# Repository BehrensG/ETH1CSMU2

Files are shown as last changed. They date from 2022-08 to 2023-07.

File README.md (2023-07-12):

# ETH1CSMU2
> Yet another poor man's SMU based on LT1970 Power Op Amp.

## What is a SMU ?

A Source Measurement Unit (SMU) is a versatile electronic instrument used in various applications, particularly in the field of electronics testing and characterization. It combines the functionalities of both a voltage source and a current measurement device.

## What is ETH1CSMU2 ?

ETH1CSMU2 is an ongoing hobby project focused on the development of a cost-effective Source Measurement Unit (SMU). The PCB has been designed in accordance with the Eurocard standard size, measuring 160x100 mm. It should be noted that the PCB is intended for integration with a Backplane, such as the [DIN41612_Backplane](https://github.com/BehrensG/DIN41612_Backplane), and is not intended for standalone operation (but it can be).
The PCB requires 24V DC supply. The device can sink and source voltage and current. Can generate a AC sine signal. The PCB includes pars of two ADCs for measurements. 2xADS868 designed the DC output mode, 2xAD7980 designed for AC output mode.

## Parameters

### DC
- Voltage output 11V (bipolar)
- Minimal set voltage step 1mV
- Current ranges 200uA, 2mA, 20mA and 200mA (bipolar)

### AC

- Sine wave generator
- Amplitude 6 V (bipolar)
- Offset 11 V (bipolar)
- Frequency 200 kHz

## Resources
- SCPI parser - https://github.com/j123b567/scpi-parser
- KiCAD - https://www.kicad.org
- STM32CubeIDE - https://www.st.com/en/development-tools/stm32cubeide.html
- POOR MAN'S SMU - https://poormanssmu.wordpress.com
- FreeRTOS - https://www.freertos.org/

## Images
<p align="center"> ETH1CSMU2 </p>

<p align="center">
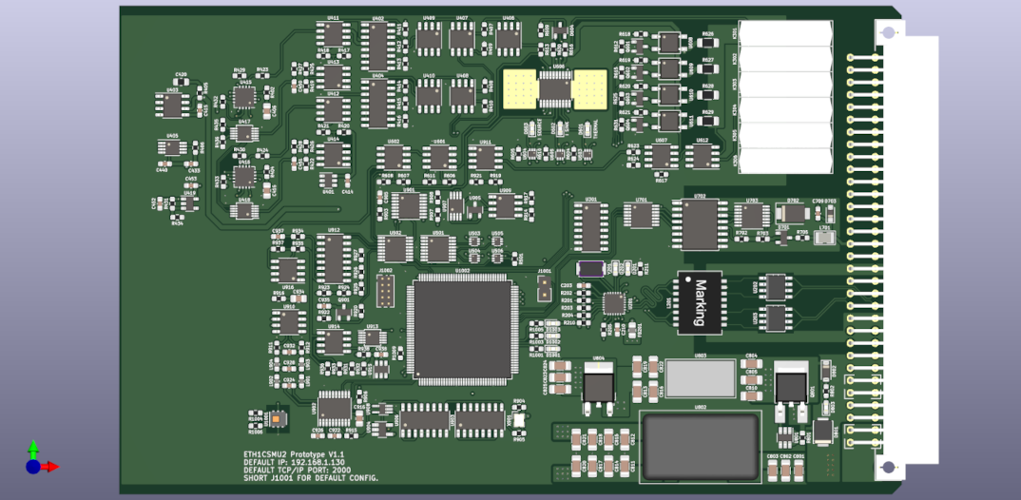
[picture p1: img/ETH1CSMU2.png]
  
 </p>

<p align="center"> Examples of the output voltages </p>

<p align="center">
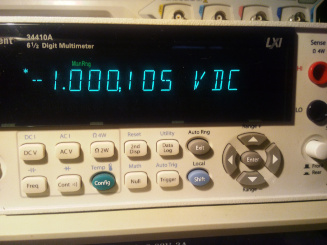
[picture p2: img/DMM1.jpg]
  
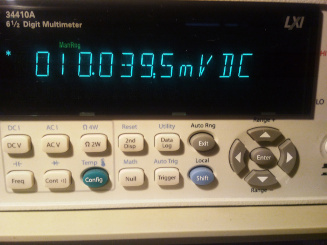
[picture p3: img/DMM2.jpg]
   
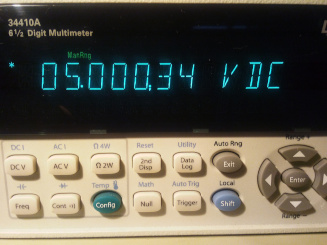
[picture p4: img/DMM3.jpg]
   
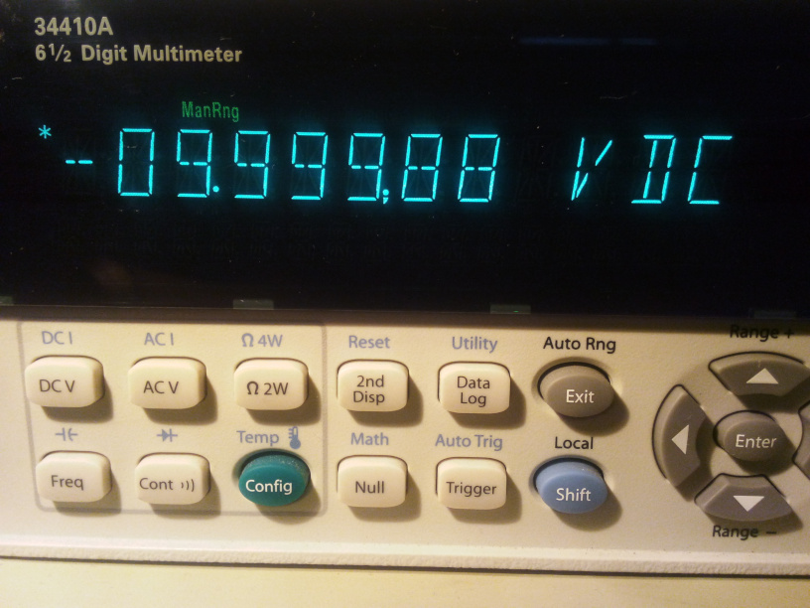
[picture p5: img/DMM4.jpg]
   
 </p>

## Status

Project is ongoing. 

#### TBD:
1. Missing code for ADCs calibration.
2. Missing code for the trigger circuit. 
3. Need to improve the AC code.
4. More images in this README file.
5. Missing SCPI commands documentation.

**<span style="color:red">NOTE</span>**: When using KiCAD project it will be required to change the schematic and PCB libraries paths.

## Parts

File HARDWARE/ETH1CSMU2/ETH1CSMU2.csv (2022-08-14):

Id | Designator | Package | Quantity | Designation | Supplier and ref
1 | C410,C421,C454,C705,C933,C301,C403,C414,C1021,C702,C455,C707,C1010,C415 | C_0603_1608Metric_Pad1.08x0.95mm_HandSolder | 14 | 1u
2 | C449,C617,C441,C903,C912,C603,C428,C419,C405,C919,C928,C601,C426,C929,C402,C507,C445,C418,C435,C606,C446,C612,C907,C429,C1022,C436,C607,C604,C610,C407,C440,C437,C1011,C508,C1018,C425,C605,C438,C704,C434,C611,C908,C1001,C923,C703,C922,C501,C442,C618,C401,C1017,C614,C911,C915,C904,C424,C1014,C901,C708,C906,C444,C417,C510,C430,C502,C608,C615,C616,C413,C918,C1016,C1012,C509,C409,C506,C921,C905,C443,C422,C1015,C926,C1020,C503,C609,C427,C1007,C431,C909,C1004,C448,C504,C1013,C408,C411,C447,C902,C423,C1009,C432,C439,C925,C412,C701,C602,C505,C613,C1019,C1002,C706,C404 | C_0603_1608Metric_Pad1.08x0.95mm_HandSolder | 110 | 100n
3 | R902,R622,R629,R424,R409,R615,R434,R423,R410,R918,R623,R613 | R_0603_1608Metric_Pad0.98x0.95mm_HandSolder | 12 | 0
4 | U604,U503,U505,U506,U603,U605,U504 | SOT-563 | 7 | SN74LVC1T45DRLR
5 | L701 | CW252016 | 1 | CW252016-R33G
6 | R924,R903,R911 | R_0603_1608Metric_Pad0.98x0.95mm_HandSolder | 3 | 68
7 | Y1001 | NX3225GD | 1 | NX5032GA-16.000M
8 | R704,R609,R914,R930,R501,R604,R605,R603,R618,R602,R619,R601,R620,R912,R617 | R_0603_1608Metric_Pad0.98x0.95mm_HandSolder | 15 | 1k
9 | R608,R610,R612 | R_0603_1608Metric_Pad0.98x0.95mm_HandSolder | 3 | 10k2/.1%
10 | C804,C801 | C_1206_3216Metric_Pad1.33x1.80mm_HandSolder | 2 | 10u/50V
11 | K304,K305,K302,K301,K306,K303 | HE360_x-5050462-8 | 6 | HE3621A0510
12 | R212 | R_0603_1608Metric_Pad0.98x0.95mm_HandSolder | 1 | 12k1
13 | U908 | MSOP-8_3x3mm_P0.65mm | 1 | MAX5217GUA+
14 | R206,R611,R211,R1010,R936,R432,R431,R403,R624,R207,R614,R430,R1009,R1002,R917,R208,R935,R701,R630,R429,R209,R401,R203 | R_0603_1608Metric_Pad0.98x0.95mm_HandSolder | 23 | 10k
15 | U1003 | MSOP-8_3x3mm_P0.65mm | 1 | 24LC08B-E/MS
16 | R202,R204,R201,R205,R925 | R_0603_1608Metric_Pad0.98x0.95mm_HandSolder | 5 | 33
17 | C824,C820,C821,C823,C822,C826,C819 | C_1206_3216Metric_Pad1.33x1.80mm_HandSolder | 7 | 1u
18 | U801 | SOT-23-6_Handsoldering | 1 | MAX5902
19 | R706 | R_0603_1608Metric_Pad0.98x0.95mm_HandSolder | 1 | 51R1
20 | D1001 | LED_0603_1608Metric_Pad1.05x0.95mm_HandSolder | 1 | BLUE
21 | R921,R923 | R_0603_1608Metric_Pad0.98x0.95mm_HandSolder | 2 | 220
22 | L904,L903,L901,L902 | L_0603_1608Metric_Pad1.05x0.95mm_HandSolder | 4 | CBMF1608T100K
23 | R414,R411 | R_0603_1608Metric_Pad0.98x0.95mm_HandSolder | 2 | 180k/0.05%
24 | U910,U612,U916 | SOIC-8_3.9x4.9mm_P1.27mm | 3 | LM7171BIM
25 | C213,C214 | C_1206_3216Metric_Pad1.33x1.80mm_HandSolder | 2 | 1n/1kV
26 | R1007,R1006,R905,R919,R1008,R906,R1004,R901 | R_0603_1608Metric_Pad0.98x0.95mm_HandSolder | 8 | 4k7
27 | R607,R606 | R_0603_1608Metric_Pad0.98x0.95mm_HandSolder | 2 | 3k4/.1%
28 | U803 | TSR2 | 1 | TSR2-2450
29 | U404,U402 | SOIC-16_3.9x9.9mm_P1.27mm | 2 | DG444DY+
30 | J1001 | PinHeader_1x02_P2.54mm_Vertical | 1 | Conn_02x01
31 | C825 | C_1206_3216Metric_Pad1.33x1.80mm_HandSolder | 1 | 10u
32 | R908,R907 | R_0603_1608Metric_Pad0.98x0.95mm_HandSolder | 2 | 200/.1%
33 | C210,C205,C202,C208,C212,C209,C211 | C_0201_0603Metric_Pad0.64x0.40mm_HandSolder | 7 | 100n
34 | C204,C201 | C_0201_0603Metric_Pad0.64x0.40mm_HandSolder | 2 | 8p
35 | Q901 | SOT-23 | 1 | FDV301N
36 | U415,U416 | QFN-16-1EP_4x4mm_P0.65mm_EP2.7x2.7mm | 2 | ADS8681IRUMT
37 | U606 | HTSSOP-20-1EP_4.4x6.5mm_P0.65mm_EP3.4x6.5mm_ThermalVias | 1 | LT1970ACFE
38 | C452,C453 | C_0603_1608Metric_Pad1.08x0.95mm_HandSolder | 2 | 2n7
39 | C207,C206 | C_0201_0603Metric_Pad0.64x0.40mm_HandSolder | 2 | 1u
40 | U610,U611,U609,U608 | AQY212GS | 4 | AQY212G2SX
41 | R703,R926 | R_0603_1608Metric_Pad0.98x0.95mm_HandSolder | 2 | 100
42 | U703 | TSSOP-14_4.4x5mm_P0.65mm | 1 | 74AC125
43 | U413,U911,U410,U409,U414 | SOIC-8_3.9x4.9mm_P1.27mm | 5 | OPA141AID
44 | C811,C814,C812 | C_1206_3216Metric_Pad1.33x1.80mm_HandSolder | 3 | 22u
45 | C932,C931,C924 | C_0603_1608Metric_Pad1.08x0.95mm_HandSolder | 3 | 1p
46 | R929 | R_0603_1608Metric_Pad0.98x0.95mm_HandSolder | 1 | 26k4
47 | D702 | D_SMB | 1 | SMBJ5.0A
48 | J301 | Socket_DIN41612-CaseC1-AC-Male-64Pin-2rows | 1 | C64AC
49 | C805,C817,C802,C810,C813,C803 | C_1206_3216Metric_Pad1.33x1.80mm_HandSolder | 6 | 4u7/50V
50 | U912 | MSOP-10_3x3mm_P0.5mm | 1 | AD5322ARMZ
51 | C203 | C_0201_0603Metric_Pad0.64x0.40mm_HandSolder | 1 | 470p
52 | U913 | SOIC-16_3.9x9.9mm_P1.27mm | 1 | DG409DY+
53 | D602,D1002,D603,D803,D601 | LED_0603_1608Metric_Pad1.05x0.95mm_HandSolder | 5 | RED
54 | D202,D1003 | LED_0603_1608Metric_Pad1.05x0.95mm_HandSolder | 2 | GREEN
55 | C450,C451 | C_0603_1608Metric_Pad1.08x0.95mm_HandSolder | 2 | 330p
56 | R427,R428 | R_0603_1608Metric_Pad0.98x0.95mm_HandSolder | 2 | 20
57 | R407,R801,R931,R408,R920 | R_0603_1608Metric_Pad0.98x0.95mm_HandSolder | 5 | 100k
58 | U403 | SOIC-8_3.9x4.9mm_P1.27mm | 1 | REF5040ID
59 | R406 | R_0603_1608Metric_Pad0.98x0.95mm_HandSolder | 1 | 82k
60 | R214,R213 | R_0603_1608Metric_Pad0.98x0.95mm_HandSolder | 2 | 270
61 | R422,R421,R418,R419 | R_0603_1608Metric_Pad0.98x0.95mm_HandSolder | 4 | 12k/.1%
62 | R904 | R_0603_1608Metric_Pad0.98x0.95mm_HandSolder | 1 | 7k5
63 | R217,R218,R216,R215 | R_0603_1608Metric_Pad0.98x0.95mm_HandSolder | 4 | 49R9
64 | R1001,R1005,R922 | R_0603_1608Metric_Pad0.98x0.95mm_HandSolder | 3 | 680
65 | U906 | SOT-23 | 1 | MAX6102EUR
66 | R932,R909,R934,R933,R910 | R_0603_1608Metric_Pad0.98x0.95mm_HandSolder | 5 | 1k/.1%
67 | U1002 | TQFP-144_20x20mm_P0.5mm | 1 | STM32F746ZG
68 | Q604,Q601,Q602,Q603 | SOT-23 | 4 | MMBT3904
69 | X901 | IQXO-791 | 1 | 830208220601
70 | C1006,C1008 | C_0603_1608Metric_Pad1.08x0.95mm_HandSolder | 2 | 2u2
71 | U502,U501 | TSSOP-16_4.4x5mm_P0.65mm | 2 | 74HCT595PW
72 | U419 | SOT-23-5 | 1 | TPS76925
73 | U405 | MSOP-8_3x3mm_P0.65mm | 1 | ADR435ARM
74 | U804 | TO-252-2 | 1 | NCV1117DT33T5G
75 | FB1001,FB201 | L_0805_2012Metric_Pad1.15x1.40mm_HandSolder | 2 | 742792031
76 | R220,R221 | R_0603_1608Metric_Pad0.98x0.95mm_HandSolder | 2 | 75/1%
77 | U407,U602,U411,U412,U601,U406,U408 | SOIC-8_3.9x4.9mm_P1.27mm | 7 | DG419DY
78 | U702 | SOIC-16W_7.5x10.3mm_P1.27mm | 1 | ADuM5402
79 | R627 | R_1206_3216Metric_Pad1.30x1.75mm_HandSolder | 1 | RQ73C2B100RBT
80 | D701 | SOT-23 | 1 | BAV99
81 | R915,R913 | R_0603_1608Metric_Pad0.98x0.95mm_HandSolder | 2 | 20k/.1%
82 | D201 | LED_0603_1608Metric_Pad1.05x0.95mm_HandSolder | 1 | YELLOW
83 | R402,R404,R405 | R_0603_1608Metric_Pad0.98x0.95mm_HandSolder | 3 | 0R22
84 | C1005,C1003 | C_0603_1608Metric_Pad1.08x0.95mm_HandSolder | 2 | 8p
85 | U701 | TSSOP-14_4.4x5mm_P0.65mm | 1 | TXB0104PW
86 | C927 | C_0805_2012Metric_Pad1.18x1.45mm_HandSolder | 1 | 4u7/OPT
87 | U905,U902 | SOIC-16_3.9x9.9mm_P1.27mm | 2 | MC74AC161DR2G
88 | R802 | R_0603_1608Metric_Pad0.98x0.95mm_HandSolder | 1 | 330
89 | R415,R412 | R_0603_1608Metric_Pad0.98x0.95mm_HandSolder | 2 | 18k/0.05%
90 | F801 | Fuse_SMD2920 | 1 | MF-LSMF185/33X
91 | C621,C620,C622,C619 | C_0603_1608Metric_Pad1.08x0.95mm_HandSolder | 4 | 10p
92 | C433,C913,C916,C930 | C_0603_1608Metric_Pad1.08x0.95mm_HandSolder | 4 | 10n
93 | U914 | SOIC-8_3.9x4.9mm_P1.27mm | 1 | TL071CDR
94 | U915,U401 | TSOT-23-6 | 2 | LT1790BCS6-2.5
95 | C818,C816,C815 | C_1206_3216Metric_Pad1.33x1.80mm_HandSolder | 3 | 4u7
96 | R928 | R_0603_1608Metric_Pad0.98x0.95mm_HandSolder | 1 | 20k8
97 | D802 | D_SOD-123 | 1 | MMSZ5249B
98 | R417,R425,R420,R426 | R_0603_1608Metric_Pad0.98x0.95mm_HandSolder | 4 | 2k49/.1%
99 | U901 | TSSOP-16_4.4x5mm_P0.65mm | 1 | DAC8565ICPW
100 | C917 | C_0603_1608Metric_Pad1.08x0.95mm_HandSolder | 1 | 68p
101 | U417,U418 | MSOP-10_3x3mm_P0.5mm | 2 | AD7980ARM
102 | U907 | SOT-353_SC-70-5_Handsoldering | 1 | SN74AUP1G79DCKR
103 | C809,C808,C807,C806 | C_1206_3216Metric_Pad1.33x1.80mm_HandSolder | 4 | 1000p/2kV
104 | R702 | R_0603_1608Metric_Pad0.98x0.95mm_HandSolder | 1 | 14k7
105 | C920,C914 | C_0603_1608Metric_Pad1.08x0.95mm_HandSolder | 2 | 100p
106 | D703 | D_SOD-323_HandSoldering | 1 | SD36C-01FTG
107 | C416,C406 | R_0805_2012Metric_Pad1.20x1.40mm_HandSolder | 2 | 22u
108 | R416,R413 | R_0603_1608Metric_Pad0.98x0.95mm_HandSolder | 2 | 2k/0.05%
109 | R705 | R_0603_1608Metric_Pad0.98x0.95mm_HandSolder | 1 | 47
110 | Y201 | NX5032GA | 1 | NX5032GA-25.000000MHZ-LN-CD-1
111 | U203,U202 | SO8E | 2 | LC03-3.3
112 | R927 | R_0603_1608Metric_Pad0.98x0.95mm_HandSolder | 1 | 200
113 | C827 | C_1206_3216Metric_Pad1.33x1.80mm_HandSolder | 1 | 100n
114 | D801 | DO_214AA_REV | 1 | SM6T30AY
115 | R433,R621 | R_0603_1608Metric_Pad0.98x0.95mm_HandSolder | 2 | OPT
116 | R210 | R_0603_1608Metric_Pad0.98x0.95mm_HandSolder | 1 | 1k5
117 | U904 | SOT-23-5_HandSoldering | 1 | SN74AHC1G14DBVT
118 | R916 | R_0603_1608Metric_Pad0.98x0.95mm_HandSolder | 1 | 1Meg
119 | R625 | R_1206_3216Metric_Pad1.30x1.75mm_HandSolder | 1 | RT1206BRD071RL
120 | U607 | SOIC-8_3.9x4.9mm_P1.27mm | 1 | INA823DT
121 | U909 | SOIC-8_3.9x4.9mm_P1.27mm | 1 | OPA2141AID
122 | C420 | R_0805_2012Metric_Pad1.20x1.40mm_HandSolder | 1 | 10u
123 | U1001 | Texas_PWSON-N6 | 1 | HDC1080
124 | U903 | TSSOP-20_4.4x6.5mm_P0.65mm | 1 | AD9834BRUZ
125 | J1002 | PinHeader_2x05_P1.27mm_Vertical | 1 | 20021111-00010T4LF
126 | R219 | R_1206_3216Metric_Pad1.30x1.75mm_HandSolder | 1 | 1M/1kV
127 | U201 | QFN-24-1EP_4x4mm_P0.5mm_EP2.6x2.6mm_ThermalVias | 1 | LAN8742A
128 | U802 | TEL12-DUAL | 1 | TEL 12-2423
129 | L201 | 749010012A | 1 | 749010012A
130 | R1003 | R_0603_1608Metric_Pad0.98x0.95mm_HandSolder | 1 | 560
131 | R628 | R_1206_3216Metric_Pad1.30x1.75mm_HandSolder | 1 | PHPA1206E1001BST
132 | C709 | C_0603_1608Metric_Pad1.08x0.95mm_HandSolder | 1 | 47p
133 | Q801 | TO-252-2_Rectifier | 1 | IRFR5410
134 | R626 | R_1206_3216Metric_Pad1.30x1.75mm_HandSolder | 1 | RP73D2B10RBTG
135 | U301 | SOIC-16_3.9x9.9mm_P1.27mm | 1 | ULN2003AIDE4
136 | C910 | C_0805_2012Metric_Pad1.18x1.45mm_HandSolder | 1 | 4u7
137 | R616 | R_0603_1608Metric_Pad0.98x0.95mm_HandSolder | 1 | 11k/.1%

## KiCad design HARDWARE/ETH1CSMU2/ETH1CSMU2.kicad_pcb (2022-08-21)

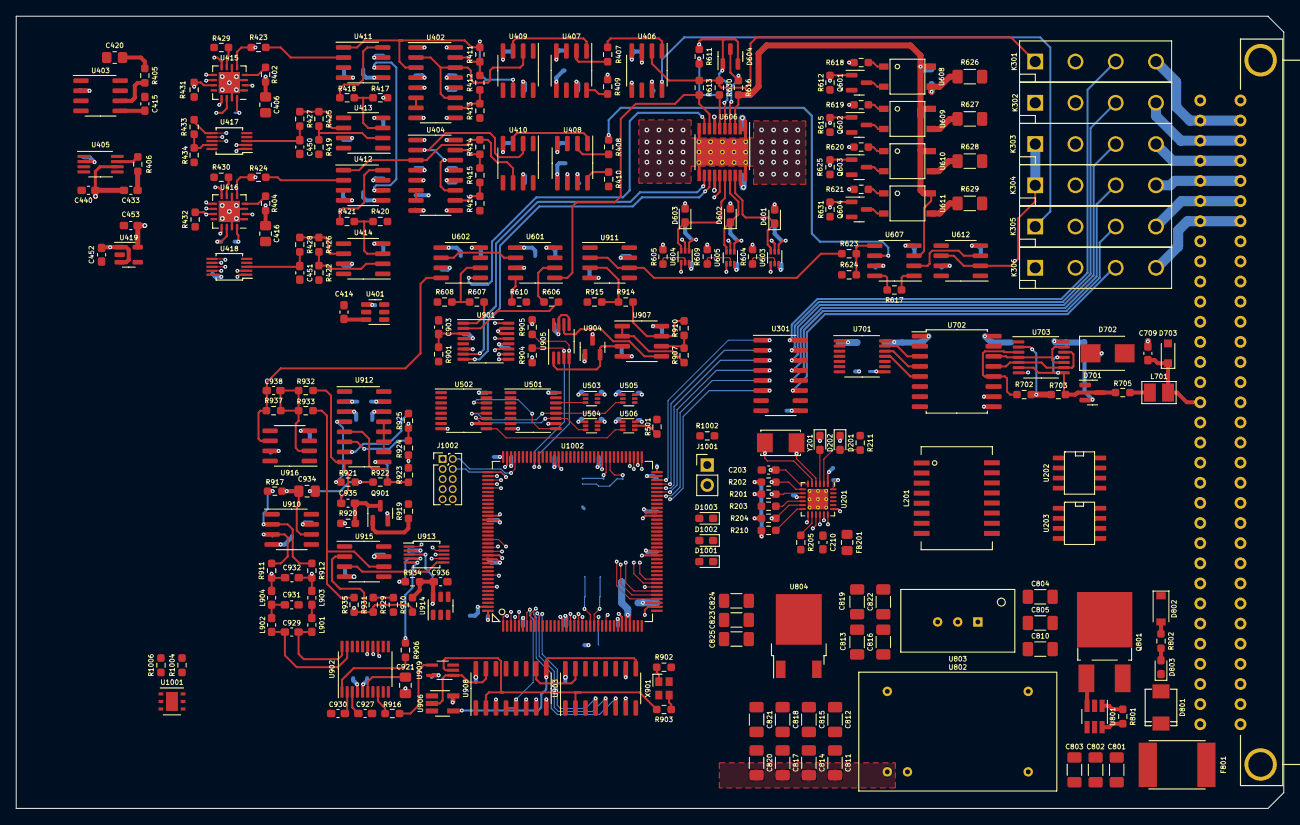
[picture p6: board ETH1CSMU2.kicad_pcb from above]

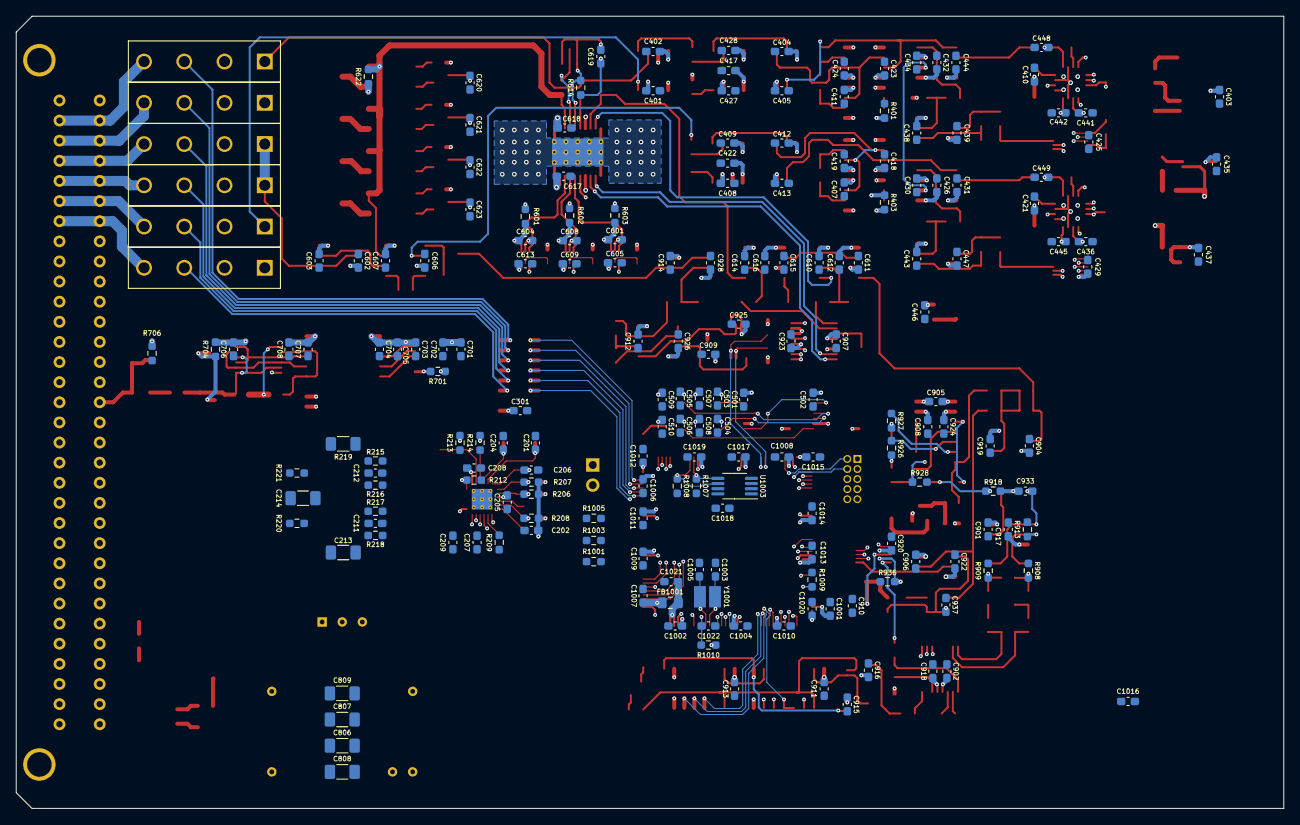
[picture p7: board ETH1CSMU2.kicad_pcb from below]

Board: 4 copper layers, 160.0 x 100.0 mm, 446 parts (191 on the bottom side), 310 nets.

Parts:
C201, C204, C1003, C1005: 8p; C_0603_1608Metric_Pad1.08x0.95mm_HandSolder
C202, C205, C208, C209, C210, C211, C212, C401, C402, C404, C405, C407, C408, C409, C411, C412, C413, C417, C418, C419, C422, C423, C424, C425, C426, C427, C428, C429, C430, C431, C432, C434, C435, C436, C437, C438, C439, C440, C441, C442, C443, C444, C445, C446, C447, C501, C502, C503, C504, C505, C506, C507, C508, C509, C510, C601, C602, C603, C604, C605, C606, C607, C608, C609, C610, C611, C612, C613, C614, C615, C616, C617, C618, C701, C703, C704, C706, C708, C901, C902, C903, C904, C905, C906, C907, C908, C909, C910, C911, C912, C913, C914, C915, C916, C917, C918, C919, C920, C922, C923, C924, C925, C926, C928, C1001, C1002, C1004, C1007, C1009, C1011, C1012, C1013, C1014, C1015, C1016, C1017, C1018, C1019, C1020, C1022: 100n; C_0603_1608Metric_Pad1.08x0.95mm_HandSolder
C203: 470p; C_0603_1608Metric_Pad1.08x0.95mm_HandSolder
C206, C207, C301, C403, C410, C414, C415, C421, C452, C453, C702, C705, C707, C936, C1010, C1021: 1u; C_0603_1608Metric_Pad1.08x0.95mm_HandSolder
C213, C214: 1n/1kV; C_1206_3216Metric_Pad1.33x1.80mm_HandSolder
C406, C416: 22u; R_0805_2012Metric_Pad1.20x1.40mm_HandSolder
C420: 10u; R_0805_2012Metric_Pad1.20x1.40mm_HandSolder
C433, C927, C930, C935: 10n; C_0603_1608Metric_Pad1.08x0.95mm_HandSolder
C448, C449: 330p; C_0603_1608Metric_Pad1.08x0.95mm_HandSolder
C450, C451: 2n7; C_0603_1608Metric_Pad1.08x0.95mm_HandSolder
C619: 1n; C_0603_1608Metric_Pad1.08x0.95mm_HandSolder
C620, C621, C622, C623: 10p; C_0603_1608Metric_Pad1.08x0.95mm_HandSolder
C709: 47p; C_0603_1608Metric_Pad1.08x0.95mm_HandSolder
C801, C804: 10u/50V; C_1206_3216Metric_Pad1.33x1.80mm_HandSolder
C802, C803, C805, C810: 4u7/50V; C_1206_3216Metric_Pad1.33x1.80mm_HandSolder
C806, C807, C808, C809: 1000p/2kV; C_1206_3216Metric_Pad1.33x1.80mm_HandSolder
C811, C812, C813: 22u; C_1206_3216Metric_Pad1.33x1.80mm_HandSolder
C814, C815, C816: 4u7; C_1206_3216Metric_Pad1.33x1.80mm_HandSolder
C817, C818, C819, C820, C821, C822, C824: 1u; C_1206_3216Metric_Pad1.33x1.80mm_HandSolder
C823: 10u; C_1206_3216Metric_Pad1.33x1.80mm_HandSolder
C825: 100n; C_1206_3216Metric_Pad1.33x1.80mm_HandSolder
C921: 4u7; C_0805_2012Metric_Pad1.18x1.45mm_HandSolder
C929, C932: 100p; C_0603_1608Metric_Pad1.08x0.95mm_HandSolder
C931: 68p; C_0603_1608Metric_Pad1.08x0.95mm_HandSolder
C933, C937, C938: 1p; C_0603_1608Metric_Pad1.08x0.95mm_HandSolder
C934: 4u7/OPT; C_0805_2012Metric_Pad1.18x1.45mm_HandSolder
C1006, C1008: 2u2; C_0603_1608Metric_Pad1.08x0.95mm_HandSolder
D201: YELLOW; LED_0603_1608Metric_Pad1.05x0.95mm_HandSolder
D202, D1003: GREEN; LED_0603_1608Metric_Pad1.05x0.95mm_HandSolder
D601, D602, D603, D803, D1002: RED; LED_0603_1608Metric_Pad1.05x0.95mm_HandSolder
D604, D701: BAV99; SOT-23
D702: SMBJ5.0A; D_SMB
D703: SD36C-01FTG; D_SOD-323_HandSoldering
D801: SM6T30AY; DO_214AA_REV
D802: MMSZ5249B; D_SOD-123
D1001: BLUE; LED_0603_1608Metric_Pad1.05x0.95mm_HandSolder
F801: MF-LSMF185/33X; Fuse_SMD2920
FB201, FB1001: 742792031; L_0805_2012Metric_Pad1.15x1.40mm_HandSolder
J301: C64AC; Socket_DIN41612-CaseC1-AC-Male-64Pin-2rows
J1001: Conn_02x01; PinHeader_1x02_P2.54mm_Vertical
J1002: 20021111-00010T4LF; PinHeader_2x05_P1.27mm_Vertical
K301, K302, K303, K304, K305, K306: HE3621A0510; HE360_x-5050462-8
L201: 749010012A
L701: CW252016-R33G; CW252016
L901, L902, L903, L904: CBMF1608T100K; L_0603_1608Metric_Pad1.05x0.95mm_HandSolder
Q601, Q602, Q603, Q604: MMBT3904; SOT-23
Q801: IRFR5410; TO-252-2_Rectifier
Q901: FDV301N; SOT-23
R201, R202, R204, R205, R925: 33; R_0603_1608Metric_Pad0.98x0.95mm_HandSolder
R203, R206, R207, R208, R209, R211, R401, R403, R429, R430, R431, R432, R612, R615, R625, R631, R701, R915, R934, R936, R1002, R1009, R1010: 10k; R_0603_1608Metric_Pad0.98x0.95mm_HandSolder
R210: 1k5; R_0603_1608Metric_Pad0.98x0.95mm_HandSolder
R212: 12k1; R_0603_1608Metric_Pad0.98x0.95mm_HandSolder
R213, R214: 270; R_0603_1608Metric_Pad0.98x0.95mm_HandSolder
R215, R216, R217, R218: 49R9; R_0603_1608Metric_Pad0.98x0.95mm_HandSolder
R219: 1M/1kV; R_1206_3216Metric_Pad1.30x1.75mm_HandSolder
R220, R221: 75/1%; R_0603_1608Metric_Pad0.98x0.95mm_HandSolder
R402, R404, R405: 0R22; R_0603_1608Metric_Pad0.98x0.95mm_HandSolder
R406: 82k; R_0603_1608Metric_Pad0.98x0.95mm_HandSolder
R407, R408, R801, R920, R935: 100k; R_0603_1608Metric_Pad0.98x0.95mm_HandSolder
R409, R410, R423, R424, R434, R614, R616, R623, R624, R630, R901, R918: 0; R_0603_1608Metric_Pad0.98x0.95mm_HandSolder
R411, R414: 180k/0.05%; R_0603_1608Metric_Pad0.98x0.95mm_HandSolder
R412, R415: 18k/0.05%; R_0603_1608Metric_Pad0.98x0.95mm_HandSolder
R413, R416: 2k/0.05%; R_0603_1608Metric_Pad0.98x0.95mm_HandSolder
R417, R420, R425, R426: 2k49/.1%; R_0603_1608Metric_Pad0.98x0.95mm_HandSolder
R418, R419, R421, R422: 12k/.1%; R_0603_1608Metric_Pad0.98x0.95mm_HandSolder
R427, R428: 20; R_0603_1608Metric_Pad0.98x0.95mm_HandSolder
R433, R622: OPT; R_0603_1608Metric_Pad0.98x0.95mm_HandSolder
R501, R601, R602, R603, R604, R605, R609, R618, R619, R620, R621, R704, R907, R910, R928: 1k; R_0603_1608Metric_Pad0.98x0.95mm_HandSolder
R606, R607: 3k4/.1%; R_0603_1608Metric_Pad0.98x0.95mm_HandSolder
R608, R610, R613: 10k2/.1%; R_0603_1608Metric_Pad0.98x0.95mm_HandSolder
R611, R703, R926: 100; R_0603_1608Metric_Pad0.98x0.95mm_HandSolder
R617: 11k/.1%; R_0603_1608Metric_Pad0.98x0.95mm_HandSolder
R626: RT1206BRD071RL; R_1206_3216Metric_Pad1.30x1.75mm_HandSolder
R627: RP73D2B10RBTG; R_1206_3216Metric_Pad1.30x1.75mm_HandSolder
R628: RQ73C2B100RBT; R_1206_3216Metric_Pad1.30x1.75mm_HandSolder
R629: PHPA1206E1001BST; R_1206_3216Metric_Pad1.30x1.75mm_HandSolder
R702: 14k7; R_0603_1608Metric_Pad0.98x0.95mm_HandSolder
R705: 47; R_0603_1608Metric_Pad0.98x0.95mm_HandSolder
R706: 51R1; R_0603_1608Metric_Pad0.98x0.95mm_HandSolder
R802: 330; R_0603_1608Metric_Pad0.98x0.95mm_HandSolder
R902, R904, R905, R919, R1004, R1006, R1007, R1008: 4k7; R_0603_1608Metric_Pad0.98x0.95mm_HandSolder
R903, R916, R924: 68; R_0603_1608Metric_Pad0.98x0.95mm_HandSolder
R906: 7k5; R_0603_1608Metric_Pad0.98x0.95mm_HandSolder
R908, R909: 200/.1%; R_0603_1608Metric_Pad0.98x0.95mm_HandSolder
R911, R912, R932, R933, R937: 1k/.1%; R_0603_1608Metric_Pad0.98x0.95mm_HandSolder
R913, R917: 20k/.1%; R_0603_1608Metric_Pad0.98x0.95mm_HandSolder
R914: 1Meg; R_0603_1608Metric_Pad0.98x0.95mm_HandSolder
R921, R923: 220; R_0603_1608Metric_Pad0.98x0.95mm_HandSolder
R922, R1001, R1005: 680; R_0603_1608Metric_Pad0.98x0.95mm_HandSolder
R927: 200; R_0603_1608Metric_Pad0.98x0.95mm_HandSolder
R929: 26k1; R_0603_1608Metric_Pad0.98x0.95mm_HandSolder
R930: 20k8; R_0603_1608Metric_Pad0.98x0.95mm_HandSolder
R931: 300; R_0603_1608Metric_Pad0.98x0.95mm_HandSolder
R1003: 560; R_0603_1608Metric_Pad0.98x0.95mm_HandSolder
U201: LAN8742A; QFN-24-1EP_4x4mm_P0.5mm_EP2.6x2.6mm_ThermalVias
U202, U203: LC03-3.3; SO8E
U301: ULN2003AIDE4; SOIC-16_3.9x9.9mm_P1.27mm
U401, U914: LT1790BCS6-2.5; TSOT-23-6
U402, U404: DG444DY+; SOIC-16_3.9x9.9mm_P1.27mm
U403: REF5040ID; SOIC-8_3.9x4.9mm_P1.27mm
U405: ADR435ARM; MSOP-8_3x3mm_P0.65mm
U406, U407, U408, U411, U412, U601, U602: DG419DY; SOIC-8_3.9x4.9mm_P1.27mm
U409, U410, U413, U414, U911: OPA141AID; SOIC-8_3.9x4.9mm_P1.27mm
U415, U416: ADS8681IRUMT; QFN-16-1EP_4x4mm_P0.65mm_EP2.7x2.7mm
U417, U418: AD7980ARM; MSOP-10_3x3mm_P0.5mm
U419: TPS76925; SOT-23-5
U501, U502: 74HCT595PW; TSSOP-16_4.4x5mm_P0.65mm
U503, U504, U505, U506, U603, U604, U605: SN74LVC1T45DRLR; SOT-563
U606: LT1970ACFE; HTSSOP-20-1EP_4.4x6.5mm_P0.65mm_EP3.4x6.5mm_ThermalVias
U607: INA823DT; SOIC-8_3.9x4.9mm_P1.27mm
U608, U609, U610, U611: AQY212G2SX; AQY212GS
U612, U910, U916: LM7171BIM; SOIC-8_3.9x4.9mm_P1.27mm
U701: TXB0104PW; TSSOP-14_4.4x5mm_P0.65mm
U702: ADuM5402; SOIC-16W_7.5x10.3mm_P1.27mm
U703: 74AC125; TSSOP-14_4.4x5mm_P0.65mm
U801: MAX5902ACEUT; SOT-23-6_Handsoldering
U802: TEL 12-2423; TEL12-DUAL
U803: TSR2-2450; TSR2
U804: NCV1117DT33T5G; TO-252-2
U901: DAC8565ICPW; TSSOP-16_4.4x5mm_P0.65mm
U902: AD9834BRUZ; TSSOP-20_4.4x6.5mm_P0.65mm
U903, U908: MC74AC161DR2G; SOIC-16_3.9x9.9mm_P1.27mm
U904: MAX6102EUR; SOT-23
U905: MAX5217GUA+; MSOP-8_3x3mm_P0.65mm
U906: SN74AHC1G14DBVT; SOT-23-5_HandSoldering
U907: OPA2141AID; SOIC-8_3.9x4.9mm_P1.27mm
U909: SN74AUP1G79DCKR; SOT-353_SC-70-5_Handsoldering
U912: DG409DY+; SOIC-16_3.9x9.9mm_P1.27mm
U913: AD5322ARMZ; MSOP-10_3x3mm_P0.5mm
U915: TL071CDR; SOIC-8_3.9x4.9mm_P1.27mm
U1001: HDC1080; Texas_PWSON-N6
U1002: STM32F746ZG; TQFP-144_20x20mm_P0.5mm
U1003: 24LC08B-E/MS; MSOP-8_3x3mm_P0.65mm
X901: 830208220601; IQXO-791
Y201: NX5032GA-25.000000MHZ-LN-CD-1; NX5032GA
Y1001: NX5032GA-16.000M; NX3225GD

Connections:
+1V25: R934.2, R936.2, U913.4 (VREFA)
+2V5PWR: C453.1, U417.2 (VDD), U418.2 (VDD), U419.5 (OUT)
+3.3V: C202.1, C205.1, C425.1, C429.1, C436.1, C441.1, C507.1, C508.1, C509.1, C510.1, C605.1, C609.1, C613.1, C701.1, C702.1, C823.1, C824.1, C825.1, C911.1, C913.1, C915.1, C916.1, C918.1, C920.1, C923.1, C925.1, C1001.1, C1002.1, C1004.1, C1007.1, C1009.1, C1010.1, C1011.1, C1012.1, C1013.1, C1014.1, C1015.1, C1016.1, C1017.1, C1018.1, C1019.1, C1020.1, D1001.2 (A), D1002.2 (A), D1003.2 (A), FB201.2, FB1001.2, J1002.1, R206.1, R207.1, R208.1, R209.1, R210.1, R429.1, R430.1, R431.1, R432.1, R701.1, R902.1, R904.1, R905.1, R1002.2, R1004.1, R1006.1, R1007.1, R1008.1, R1010.1, U201.9 (VDDIO), U415.14 (DVDD), U416.14 (DVDD), U417.10 (VIO), U418.10 (VIO), U503.6 (VCCB), U504.6 (VCCB), U505.6 (VCCB), U506.6 (VCCB), U603.6 (VCCB), U604.6 (VCCB), U605.6 (VCCB), U701.1 (VCCA), U804.2 (VO), U901.12 (IOVDD), U902.5 (DVDD), U903.1 (~MR), U903.7 (CEP), U903.10 (CET), U903.16 (VCC), U905.5 (~AUX), U905.7 (VDD), U906.5 (VCC), U908.1 (~MR), U908.3 (P0), U908.6 (P3), U908.7 (CEP), U908.16 (VCC), U909.5 (VCC), U913.2 (VDD), U1001.5 (VCC), U1002.6 (VBAT), U1002.17 (VDD), U1002.30 (VDD), U1002.39 (VDD), U1002.52 (VDD), U1002.62 (VDD), U1002.72 (VDD), U1002.84 (VDD), U1002.95 (VDDUSB), U1002.108 (VDD), U1002.121 (VDD), U1002.131 (VDD), U1002.143 (PDR_ON), U1002.144 (VDD), U1003.8 (VCC), X901.4 (VDD)
+4V: R405.1, U403.6 (Vout), U415.2 (REFIO), U416.2 (REFIO)
+5V: C301.1, C403.1, C407.1, C411.1, C417.1, C422.1, C426.1, C432.1, C437.1, C442.1, C445.1, C452.1, C501.1, C502.1, C503.1, C504.1, C505.1, C506.1, C601.1, C604.1, C608.1, C612.1, C616.1, C703.1, C704.1, C705.1, C813.1, C816.1, C819.1, C822.1, C902.1, C905.1, C907.1, C909.1, C927.1, K301.2, K302.2, K303.2, K304.2, K305.2, K306.2, R401.2, R403.2, R501.2, R601.1, R602.1, R603.1, R604.2, R605.2, R609.2, R618.1, R619.1, R620.1, R621.1, R920.1, U301.9 (COM), U402.12 (VL), U403.2 (Vin), U404.12 (VL), U406.5 (VL), U407.5 (VL), U408.5 (VL), U411.5 (VL), U412.5 (VL), U415.16 (AVDD), U416.16 (AVDD), U419.1 (IN), U419.3 (~EN), U501.10 (~SRCLR), U501.16 (VCC), U502.10 (~SRCLR), U502.16 (VCC), U503.1 (VCCA), U504.1 (VCCA), U505.1 (VCCA), U506.1 (VCCA), U601.5 (VL), U602.5 (VL), U603.1 (VCCA), U604.1 (VCCA), U605.1 (VCCA), U701.14 (VCCB), U702.1 (VDD1), U803.3 (VO), U804.3 (VI), U901.4 (AVDD), U902.4 (AVDD), U904.1 (IN), U912.2 (EN)
+5VREF: C433.1, C440.1, U405.6 (VOUT), U417.1 (REF), U418.1 (REF)
+5V_TRIG: C706.1, C707.1, C708.1, R704.1, U702.10 (VSEL), U702.16 (VISO), U703.14 (VCC)
+15V: C402.1, C405.1, C409.1, C413.1, C419.1, C424.1, C428.1, C431.1, C435.1, C439.1, C444.1, C446.1, C447.1, C602.1, C606.1, C610.1, C614.1, C617.1, C807.2, C809.2, C811.1, C814.1, C817.1, C820.1, C901.1, C904.1, C906.1, C908.1, C910.1, C912.1, C914.1, U401.4 (Vin), U402.13 (V+), U404.13 (V+), U405.2 (VIN), U406.4 (V+), U407.4 (V+), U408.4 (V+), U409.7 (V+), U410.7 (V+), U411.4 (V+), U412.4 (V+), U413.7 (V+), U414.7 (V+), U601.4 (V+), U602.4 (V+), U606.7 (VCC), U606.19 (V+), U607.7 (V+), U612.7 (V+), U802.9 (+VOUT), U907.8 (V+), U910.7 (V+), U911.7 (V+), U912.14 (V+), U914.4 (Vin), U915.7 (V+), U916.7 (V+)
+24V: F801.2, J301.A31 (31A), J301.A32 (32A), J301.C31 (31C), J301.C32 (32C)
-15V: C401.1, C404.1, C408.1, C412.1, C418.1, C423.1, C427.1, C430.1, C434.1, C438.1, C443.1, C603.1, C607.1, C611.1, C615.1, C618.1, C806.2, C808.2, C812.2, C815.2, C818.2, C821.2, C917.1, C919.1, C922.1, C924.1, C926.1, C928.1, U402.4 (V-), U404.4 (V-), U406.7 (V-), U407.7 (V-), U408.7 (V-), U409.4 (V-), U410.4 (V-), U411.7 (V-), U412.7 (V-), U413.4 (V-), U414.4 (V-), U601.7 (V-), U602.7 (V-), U606.1 (VEE), U606.2 (V-), U606.10 (VEE), U606.11 (VEE), U606.20 (VEE), U606.21 (VEE), U607.4 (V-), U612.4 (V-), U802.10 (-VOUT), U907.4 (V-), U910.4 (V-), U911.4 (V-), U912.3 (V-), U915.4 (V-), U916.4 (V-)
/Connect/A: J301.A2 (2A), J301.C2 (2C), K301.4
/Connect/B: J301.A3 (3A), J301.C3 (3C), K302.4
/Connect/C: J301.A4 (4A), J301.C4 (4C), K303.4
/Connect/CXN_REL1: U301.1 (I1), U1002.70 (PB11,TIM2_CH4,I2C2_SDA,DFSDM1_CKIN7,USA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)
/Connect/CXN_REL2: U301.2 (I2), U1002.69 (PB10,TIM2_CH3,I2C2_SCL,SPI2_SCK,I2S2_CK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)
/Connect/CXN_REL3: U301.3 (I3), U1002.68 (PE15,TIM1_BKIN,FMC_D12,LCD_R7,EVENTOUT)
/Connect/CXN_REL4: U301.4 (I4), U1002.67 (PE14,TIM1_CH4,SPI4_MOSI,SAI2_MCLK_B,FMC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)
/Connect/CXN_REL5: U301.5 (I5), U1002.66 (PE13,TIM1_CH3,SPI4_MISO,DFSDM1_CKIN5,SA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)
/Connect/CXN_REL6: U301.6 (I6), U1002.65 (PE12,TIM1_CH3N,SPI4_SCK,DFSDM1_DATIN5,S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)
/Connect/D: J301.A5 (5A), J301.C5 (5C), K304.4
/Connect/E: J301.A6 (6A), J301.C6 (6C), K305.4
/Connect/EXT_TRIG: C709.1, D703.1 (A1), J301.A16 (16A), L701.1
/Connect/F: J301.A7 (7A), J301.C7 (7C), K306.4
/Connect/GUARD: K303.1, K304.1, U612.2 (-), U612.6
/Connect/RX+: J301.A20 (20A), U203.8
/Connect/RX-: J301.A21 (21A), U203.5
/Connect/TX+: J301.C20 (20C), U202.8
/Connect/TX-: J301.C21 (21C), U202.5
/Connect/VOLT_MEAS_SENS: K305.1, U406.8
/Connect/VOUT_OUT: K301.1, R613.2, R626.2, R627.2, R628.2, R629.2, R630.1, U406.2, U607.2 (-), U612.3 (+)
/Control/ATT_A0: U502.3 (QD), U912.1 (A0)
/Control/ATT_A1: U502.4 (QE), U912.16 (A1)
/Control/C_AZ: U408.6, U501.7 (QH)
/Control/C_G1: U404.1, U501.4 (QE)
/Control/C_G10: U404.16, U501.5 (QF)
/Control/C_G100: U404.9, U501.6 (QG)
/Control/DDS_LPF: R919.2, U502.5 (QF)
/Control/MCU_ENA: U502.15 (QA), U606.15 (ENA)
/Control/SING_SEL: U502.2 (QC), U601.6, U602.6
/Control/SR_CLK: U504.4 (B), U1002.117 (PD3,DFSDM1_CKOUT,SPI2_SCK,I2S2_CK,DFSDM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)
/Control/SR_DAT: U503.4 (B), U1002.118 (PD4,DFSDM1_CKIN0,USART2_RTS,FMC_NOE,EVE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)
/Control/SR_LAT: U505.4 (B), U1002.119 (PD5,USART2_TX,FMC_NWE,EVENTOUT)
/Control/SR_OUT: U506.4 (B), U1002.122 (PD6,DFSDM1_CKIN4,SPI3_MOSI,I2S3_SD,SAI1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)
/Control/VMEAS_SEL: U406.6, U502.1 (QB)
/Control/V_AZ: U407.6, U501.3 (QD)
/Control/V_G1: U402.1, U501.15 (QA)
/Control/V_G10: U402.16, U501.1 (QB)
/Control/V_G100: U402.9, U501.2 (QC)
/Ethernet/ETH_RXN: L201.8 (RD-), R218.2, U201.22 (RXN)
/Ethernet/ETH_RXP: L201.6 (RD+), R217.2, U201.23 (RXP)
/Ethernet/ETH_TXN: L201.3 (TD-), R216.2, U201.20 (TXN)
/Ethernet/ETH_TXP: L201.1 (TD+), R215.2, U201.21 (TXP)
/Ethernet/MDIO: R210.2, U201.12 (MDIO), U1002.36 (PA2,TIM2_CH3,TIM5_CH3,TIM9_CH1,USART2_T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)
/Ethernet/MODE0: R201.1, R206.2, U201.8 (RXD0/MODE0)
/Ethernet/MODE1: R202.1, R207.2, U201.7 (RXD1/MODE1)
/Ethernet/MODE2: R204.1, R208.2, U201.11 (CRS_DV/MODE2)
/Ethernet/REFCLK0: R205.1, R209.2, U201.14 (~INT/REFCLK0)
/Ethernet/REF_CLK: R205.2, U1002.35 (PA1,TIM2_CH2,TIM5_CH2,UART2_RTS,UART4_R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)
/Ethernet/RMII_CRS_DV: R204.2, U1002.43 (PA7,TIM1_CH1N,TIM3_CH2,TIM8_CH1N,SPI1_M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)
/Ethernet/RMII_MDC: U201.13 (MDC), U1002.27 (PC1,TRACED0,_DFSDM1_DATIN0,SPI2_MOSI,I2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)
/Ethernet/RMII_RXD0: R201.2, U1002.44 (PC4,DFSDM1_CKIN2,I2S1_MCK,SPDIF_RX2,ETH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)
/Ethernet/RMII_RXD1: R202.2, U1002.45 (PC5,DFSDM1_DATIN2,SPDIF_RX3,ETH_MII_RXD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)
/Ethernet/RMII_TXD0: U201.17 (TXD0), U1002.128 (PG13,TRACED0,LPTIM1_OUT,SPI6_SCK,USART6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)
/Ethernet/RMII_TXD1: U201.18 (TXD1), U1002.129 (PG14,TRACED1,LPTIM1_ETR,SPI6_MOSI,USART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)
/Ethernet/RMII_TXEN: U201.16 (TXEN), U1002.126 (PG11,SPI1_SCK,I2S1_CK,SPDIF_RX0,SDMMC2_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)
/Frontend/CURR_MEAS: R408.2, U607.6
/Frontend/CURR_SENS_1R: Q601.3 (C), U608.2
/Frontend/CURR_SENS_1kR: Q604.3 (C), U611.2
/Frontend/CURR_SENS_10R: Q602.3 (C), U609.2
/Frontend/CURR_SENS_100R: Q603.3 (C), U610.2
/Frontend/FGEN: C938.2, R937.2, U602.8, U916.6
/Frontend/FILTER_LIM: C619.1, D604.1 (K), D604.2 (A), R611.1, R614.2, U606.5 (FILTER)
/Frontend/MCU_CURR_SENS_1R: R612.1, U1002.93 (PG8,SPI6_NSS,SPDIF_RX2,USART6_RTS,ETH_P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)
/Frontend/MCU_CURR_SENS_1kR: R631.1, U1002.90 (PG5,FMC_A15,FMC_BA1,EVENTOUT)
/Frontend/MCU_CURR_SENS_10R: R615.1, U1002.92 (PG7,SAI1_MCLK_A,USART6_CK,FMC_INT,DCMI_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)
/Frontend/MCU_CURR_SENS_100R: R625.1, U1002.91 (PG6,FMC_NE3,DCMI_D12,LCD_R7,EVENTOUT)
/Frontend/MCU_nISNK: U605.4 (B), U1002.53 (PF13,I2C4_SMBA,DFSDM1_DATIN6,FMC_A7,EVE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)
/Frontend/MCU_nISRC: U604.4 (B), U1002.54 (PF14,I2C4_SCL,DFSDM1_CKIN6,FMC_A8,EVENT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)
/Frontend/MCU_nTDS: U603.4 (B), U1002.55 (PF15,I2C4_SDA,FMC_A9,EVENTOUT)
/Frontend/SENS+_LIM: D604.3 (K), R616.1, U606.4 (SENSE+)
/Frontend/SENS-_LIM: C619.2, R611.2, R614.1, R630.2, U606.6 (SENSE-)
/Frontend/VC_+IN: R607.1, U901.1 (VOUTA)
/Frontend/VC_-IN: R606.1, U901.2 (VOUTB)
/Frontend/VC_SINK: U606.12 (VC_SINK), U901.7 (VOUTC)
/Frontend/VC_SRC: U606.13 (VC_SRC), U901.8 (VOUTD)
/Frontend/VOUT_OFFSET: R623.2, U911.2 (-), U911.6
/Frontend/nISNK: D602.1 (K), U605.3 (A), U606.17 (~ISNK)
/Frontend/nISRC: D603.1 (K), U604.3 (A), U606.16 (~ISRC)
/Frontend/nTDS: D601.1 (K), U603.3 (A), U606.18 (~TSD)
/MCU/ADC1_RVS1: U415.13 (RVS), U1002.34 (PA0,TIM2_CH1,TIM2_ETR,TIM5_CH1,TIM8_ETR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)
/MCU/ADC1_RVS2: U416.13 (RVS), U1002.37 (PA3,TIM2_CH4,TIM5_CH4,TIM9_CH2,USART2_R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)
/MCU/DAC1_LDAC: U901.16 (LDAC), U1002.58 (PE7,TIM1_ETR,DFSDM1_DATIN2,UART7_RX,QUA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)
/MCU/DAC1_~RST: U901.13 (~RST), U1002.64 (PE11,TIM1_CH2,SPI4_NSS,DFSDM1_CKIN4,SAI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)
/MCU/DAC2_~LDAC: U913.1 (~LDAC), U1002.22 (PF10,QUADSPI_CLK,DCMI_D11,LCD_DE,EVENTO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)
/MCU/DDS_DIV2: U903.4 (P1), U1002.10 (PF0,I2C2_SDA,FMC_A0,EVENTOUT)
/MCU/DDS_DIV4: U903.5 (P2), U1002.9 (PC15,EVENTOUT,OSC32_OUT)
/MCU/DDS_DIV8: U903.6 (P3), U1002.8 (PC14,EVENTOUT,OSC32_IN)
/MCU/EEPROM_SCL: R1008.2, U1002.81 (PD12,TIM4_CH1,LPTIM1_IN1,I2C4_SCL,USART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), U1003.6 (SCL)
/MCU/EEPROM_SDA: R1007.2, U1002.82 (PD13,TIM4_CH2,LPTIM1_OUT,I2C4_SDA,QUADS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), U1003.5 (SDA)
/MCU/EEPROM_WP: U1002.80 (PD11,I2C4_SMBA,USART3_CTS,QUADSPI_BK1_I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), U1003.7 (WP)
/MCU/LED_BLUE: R1001.1, U1002.123 (PD7,DFSDM1_DATIN4,SPI1_MOSI,I2S1_SD,DFS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)
/MCU/LED_GREEN: R1005.1, U1002.125 (PG10,SPI1_NSS,I2S1_WS,LCD_G3,SAI2_SD_B,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)
/MCU/LED_RED: R1003.1, U1002.124 (PG9,SPI1_MISO,SPDIF_RX3,USART6_RX,QUADS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)
/MCU/MCU_DEFAULT: J1001.1, R1002.1, U1002.116 (PD2,TRACED2,TIM3_ETR,UART5_RX,SDMMC1_CM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)
/MCU/MCU_VDDA: C1021.1, FB1001.1, U1002.32 (VREF+), U1002.33 (VDDA)
/MCU/NRST: C1022.1, J1002.10, R1010.2, U201.15 (~RST), U1002.25 (NRST)
/MCU/SENS_SCL: R904.2, R1004.2, U905.3 (SCL), U1001.6 (SCL), U1002.100 (PA8,MCO1,TIM1_CH1,TIM8_BKIN2,I2C3_SCL,U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)
/MCU/SENS_SDA: R905.2, R1006.2, U905.4 (SDA), U1001.1 (SDA), U1002.99 (PC9,MCO2,TIM3_CH4,TIM8_CH4,I2C3_SDA,I2S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)
/MCU/SPI1_MISO: R432.2, U416.11 (SDO-0), U1002.42 (PA6,TIM1_BKIN,TIM3_CH1,TIM8_BKIN,SPI1_M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)
/MCU/SPI1_MOSI: U415.8 (SDI), U1002.135 (PB5,UART5_RX,TIM3_CH2,I2C1_SMBA,SPI1_MO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)
/MCU/SPI1_NSS: U415.9 (CONVST/~CS), U416.9 (CONVST/~CS), U1002.40 (PA4,SPI1_NSS,I2S1_WS,SPI3_NSS,I2S3_WS,U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)
/MCU/SPI1_SCK: U415.10 (SCLK), U416.10 (SCLK), U1002.41 (PA5,TIM2_CH1,TIM2_ETR,TIM8_CH1N,SPI1_SC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)
/MCU/SPI2_MOSI: U901.11 (DIN), U1002.76 (PB15,RTC_REFIN,TIM1_CH3N,TIM8_CH3N,USAR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)
/MCU/SPI2_NSS: U901.9 (~SYNC), U1002.73 (PB12,TIM1_BKIN,I2C2_SMBA,SPI2_NSS,I2S2_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)
/MCU/SPI2_SCK: U901.10 (SCLK), U1002.74 (PB13,TIM1_CH1N,SPI2_SCK,I2S2_CK,DFSDM1_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)
/MCU/SPI3_MOSI: U902.13 (SDATA), U1002.113 (PC12,TRACED3,SPI3_MOSI,I2S3_SD,USART3_C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)
/MCU/SPI3_NSS: U902.15 (~FSYNC), U1002.110 (PA15,JTDI,TIM2_CH1,TIM2_ETR,HDMI_CEC,SP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)
/MCU/SPI3_SCK: U902.14 (SCLK), U1002.111 (PC10,DFSDM1_CKIN5,SPI3_SCK,I2S3_CK,USAR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)
/MCU/SPI4_MISO: U418.7 (SDO), U1002.4 (PE5,TRACED2,TIM9_CH1,SPI4_MISO,SAI1_SCK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)
/MCU/SPI4_NSS: R433.1, U417.6 (CNV), U418.6 (CNV), U1002.3 (PE4,TRACED1,SPI4_NSS,SAI1_FS_A,DFSDM1_D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)
/MCU/SPI4_SCK: U417.8 (SCLK), U418.8 (SCLK), U1002.1 (PE2,TRACECLK,SPI4_SCK,SAI1_MCLK_A,QUADS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)
/MCU/SPI5_MOSI: U913.9 (DIN), U1002.21 (PF9,SPI5_MOSI,SAI1_FS_B,UART7_CTS,TIM14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)
/MCU/SPI5_NSS: U913.7 (~SYNC), U1002.18 (PF6,TIM10_CH1,SPI5_NSS,SAI1_SD_B,UART7_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)
/MCU/SPI5_SCK: U913.8 (SCLK), U1002.19 (PF7,TIM11_CH1,SPI5_SCK,SAI1_MCLK_B,UART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)
/MCU/TCK_SWCLK: J1002.4, U1002.109 (PA14,JTCK-SWCLK,EVENTOUT)
/MCU/TMS_SWDIO: J1002.2, U1002.105 (PA13,JTMS-SWDIO,EVENTOUT)
/MCU/TRIG_EN: U701.2 (A1), U1002.59 (PE8,TIM1_CH1N,DFSDM1_CKIN2,UART7_TX,QUA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)
/MCU/TRIG_IN: U701.4 (A3), U1002.63 (PE10,TIM1_CH2N,DFSDM1_DATIN4,UART7_CTS,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)
/MCU/TRIG_OUT: U701.3 (A2), U1002.60 (PE9,TIM1_CH1,DFSDM1_CKOUT,UART7_RTS,QUA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)
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

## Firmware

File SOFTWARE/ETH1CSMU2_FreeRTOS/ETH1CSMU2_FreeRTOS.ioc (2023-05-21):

#MicroXplorer Configuration settings - do not modify
CAD.formats=
CAD.pinconfig=
CAD.provider=
CORTEX_M7.CPU_DCache=Disabled
CORTEX_M7.CPU_ICache=Disabled
CORTEX_M7.IPParameters=CPU_ICache,CPU_DCache,MPU_Control
CORTEX_M7.MPU_Control=__NULL
Dma.Request0=SPI4_RX
Dma.RequestsNb=1
Dma.SPI4_RX.0.Direction=DMA_PERIPH_TO_MEMORY
Dma.SPI4_RX.0.FIFOMode=DMA_FIFOMODE_DISABLE
Dma.SPI4_RX.0.Instance=DMA2_Stream0
Dma.SPI4_RX.0.MemDataAlignment=DMA_MDATAALIGN_HALFWORD
Dma.SPI4_RX.0.MemInc=DMA_MINC_ENABLE
Dma.SPI4_RX.0.Mode=DMA_NORMAL
Dma.SPI4_RX.0.PeriphDataAlignment=DMA_PDATAALIGN_HALFWORD
Dma.SPI4_RX.0.PeriphInc=DMA_PINC_DISABLE
Dma.SPI4_RX.0.Priority=DMA_PRIORITY_HIGH
Dma.SPI4_RX.0.RequestParameters=Instance,Direction,PeriphInc,MemInc,PeriphDataAlignment,MemDataAlignment,Mode,Priority,FIFOMode
ETH.IPParameters=MediaInterface
ETH.MediaInterface=HAL_ETH_RMII_MODE
FREERTOS.FootprintOK=true
FREERTOS.IPParameters=Tasks01,configMINIMAL_STACK_SIZE,configUSE_NEWLIB_REENTRANT,configTOTAL_HEAP_SIZE,FootprintOK,Queues01,configGENERATE_RUN_TIME_STATS,configUSE_STATS_FORMATTING_FUNCTIONS,configENABLE_FPU,configTIMER_TASK_STACK_DEPTH
FREERTOS.Queues01=QueueLED,1,uint8_t,0,Static,QueueLEDBuffer,QueueLEDControlBlock;QueueTrigger,1,uint8_t,0,Dynamic,NULL,NULL
FREERTOS.Tasks01=defaultTask,24,254,StartDefaultTask,Default,NULL,Dynamic,NULL,NULL;LEDTask,8,128,StartLEDTask,Default,NULL,Dynamic,NULL,NULL;TriggerTask,8,254,StartTriggerTask,Default,NULL,Dynamic,NULL,NULL
FREERTOS.configENABLE_FPU=1
FREERTOS.configGENERATE_RUN_TIME_STATS=1
FREERTOS.configMINIMAL_STACK_SIZE=128
FREERTOS.configTIMER_TASK_STACK_DEPTH=254
FREERTOS.configTOTAL_HEAP_SIZE=60000
FREERTOS.configUSE_NEWLIB_REENTRANT=1
FREERTOS.configUSE_STATS_FORMATTING_FUNCTIONS=1
File.Version=6
GPIO.groupedBy=Group By Peripherals
I2C3.IPParameters=Timing
I2C3.Timing=0x20404768
I2C4.IPParameters=Timing
I2C4.Timing=0x20404768
KeepUserPlacement=false
LWIP.BSP.number=1
LWIP.CMSIS_VERSION-Enabled=1
LWIP.DEFAULT_THREAD_STACKSIZE=2048
LWIP.GATEWAY_ADDRESS=192.168.001.001
LWIP.IPParameters=LWIP_DHCP,IP_ADDRESS,NETMASK_ADDRESS,GATEWAY_ADDRESS,CMSIS_VERSION-Enabled,LWIP_DBG_MIN_LEVEL,MEM_SIZE,TCPIP_THREAD_STACKSIZE,DEFAULT_THREAD_STACKSIZE
LWIP.IP_ADDRESS=192.168.001.130
LWIP.LWIP_DBG_MIN_LEVEL=LWIP_DBG_LEVEL_ALL
LWIP.LWIP_DHCP=0
LWIP.MEM_SIZE=3200
LWIP.NETMASK_ADDRESS=255.255.255.000
LWIP.TCPIP_THREAD_STACKSIZE=2048
LWIP.Version=v2.1.2_Cube
LWIP0.BSP.STBoard=false
LWIP0.BSP.api=BSP_COMPONENT_DRIVER
LWIP0.BSP.component=LAN8742
LWIP0.BSP.condition=
LWIP0.BSP.instance=LAN8742
LWIP0.BSP.ip=
LWIP0.BSP.mode=
LWIP0.BSP.name=Driver_PHY
LWIP0.BSP.semaphore=S_LAN8742
LWIP0.BSP.solution=LAN8742
Mcu.CPN=STM32F746ZGT6
Mcu.Family=STM32F7
Mcu.IP0=CORTEX_M7
Mcu.IP1=DMA
Mcu.IP10=SPI2
Mcu.IP11=SPI3
Mcu.IP12=SPI4
Mcu.IP13=SPI5
Mcu.IP14=SYS
Mcu.IP15=TIM3
Mcu.IP2=ETH
Mcu.IP3=FREERTOS
Mcu.IP4=I2C3
Mcu.IP5=I2C4
Mcu.IP6=LWIP
Mcu.IP7=NVIC
Mcu.IP8=RCC
Mcu.IP9=SPI1
Mcu.IPNb=16
Mcu.Name=STM32F746ZGTx
Mcu.Package=LQFP144
Mcu.Pin0=PE2
Mcu.Pin1=PE4
Mcu.Pin10=PF9
Mcu.Pin11=PC1
Mcu.Pin12=PA1
Mcu.Pin13=PA2
Mcu.Pin14=PA4
Mcu.Pin15=PA5
Mcu.Pin16=PA6
Mcu.Pin17=PA7
Mcu.Pin18=PC4
Mcu.Pin19=PC5
Mcu.Pin2=PE5
Mcu.Pin20=PB2
Mcu.Pin21=PF11
Mcu.Pin22=PF12
Mcu.Pin23=PE7
Mcu.Pin24=PE8
Mcu.Pin25=PE9
Mcu.Pin26=PE10
Mcu.Pin27=PE12
Mcu.Pin28=PE13
Mcu.Pin29=PE14
Mcu.Pin3=PC13
Mcu.Pin30=PE15
Mcu.Pin31=PB10
Mcu.Pin32=PB11
Mcu.Pin33=PB12
Mcu.Pin34=PB13
Mcu.Pin35=PB14
Mcu.Pin36=PB15
Mcu.Pin37=PD9
Mcu.Pin38=PD10
Mcu.Pin39=PD11
Mcu.Pin4=PC14/OSC32_IN
Mcu.Pin40=PD12
Mcu.Pin41=PD13
Mcu.Pin42=PD14
Mcu.Pin43=PD15
Mcu.Pin44=PG2
Mcu.Pin45=PG3
Mcu.Pin46=PG4
Mcu.Pin47=PG5
Mcu.Pin48=PG6
Mcu.Pin49=PG7
Mcu.Pin5=PC15/OSC32_OUT
Mcu.Pin50=PG8
Mcu.Pin51=PC9
Mcu.Pin52=PA8
Mcu.Pin53=PA11
Mcu.Pin54=PA12
Mcu.Pin55=PA13
Mcu.Pin56=PA14
Mcu.Pin57=PA15
Mcu.Pin58=PC10
Mcu.Pin59=PC11
Mcu.Pin6=PF0
Mcu.Pin60=PC12
Mcu.Pin61=PD0
Mcu.Pin62=PD1
Mcu.Pin63=PG11
Mcu.Pin64=PG12
Mcu.Pin65=PG13
Mcu.Pin66=PG14
Mcu.Pin67=PB5
Mcu.Pin68=VP_FREERTOS_VS_CMSIS_V2
Mcu.Pin69=VP_LWIP_VS_Enabled
Mcu.Pin7=PF6
Mcu.Pin70=VP_SYS_VS_tim2
Mcu.Pin71=VP_TIM3_VS_ClockSourceINT
Mcu.Pin8=PF7
Mcu.Pin9=PF8
Mcu.PinsNb=72
Mcu.ThirdPartyNb=0
Mcu.UserConstants=
Mcu.UserName=STM32F746ZGTx
MxCube.Version=6.8.0
MxDb.Version=DB.6.0.80
NVIC.BusFault_IRQn=true\:0\:0\:false\:false\:true\:false\:false\:false\:false
NVIC.DMA2_Stream0_IRQn=true\:5\:0\:false\:false\:true\:true\:false\:true\:true
NVIC.DebugMonitor_IRQn=true\:0\:0\:false\:false\:true\:false\:false\:false\:false
NVIC.ETH_IRQn=true\:5\:0\:false\:false\:true\:true\:false\:true\:true
NVIC.ForceEnableDMAVector=true
NVIC.HardFault_IRQn=true\:0\:0\:false\:false\:true\:false\:false\:false\:false
NVIC.MemoryManagement_IRQn=true\:0\:0\:false\:false\:true\:false\:false\:false\:false
NVIC.NonMaskableInt_IRQn=true\:0\:0\:false\:false\:true\:false\:false\:false\:false
NVIC.PendSV_IRQn=true\:15\:0\:false\:false\:false\:true\:false\:false\:false
NVIC.PriorityGroup=NVIC_PRIORITYGROUP_4
NVIC.SVCall_IRQn=true\:0\:0\:false\:false\:false\:false\:false\:false\:false
NVIC.SavedPendsvIrqHandlerGenerated=true
NVIC.SavedSvcallIrqHandlerGenerated=true
NVIC.SavedSystickIrqHandlerGenerated=true
NVIC.SysTick_IRQn=true\:15\:0\:false\:false\:false\:true\:false\:true\:false
NVIC.TIM2_IRQn=true\:0\:0\:true\:false\:true\:false\:false\:true\:true
NVIC.TimeBase=TIM2_IRQn
NVIC.TimeBaseIP=TIM2
NVIC.UsageFault_IRQn=true\:0\:0\:false\:false\:true\:false\:false\:false\:false
PA1.Mode=RMII
PA1.Signal=ETH_REF_CLK
PA11.GPIOParameters=PinState,GPIO_Label
PA11.GPIO_Label=DAC1_nRST
PA11.Locked=true
PA11.PinState=GPIO_PIN_SET
PA11.Signal=GPIO_Output
PA12.GPIOParameters=GPIO_Label
PA12.GPIO_Label=DAC1_LDAC
PA12.Locked=true
PA12.Signal=GPIO_Output
PA13.Mode=Serial_Wire
PA13.Signal=SYS_JTMS-SWDIO
PA14.Mode=Serial_Wire
PA14.Signal=SYS_JTCK-SWCLK
PA15.GPIOParameters=PinState,GPIO_Label
PA15.GPIO_Label=SPI3_NSS
PA15.Locked=true
PA15.PinState=GPIO_PIN_SET
PA15.Signal=GPIO_Output
PA2.Mode=RMII
PA2.Signal=ETH_MDIO
PA4.GPIOParameters=PinState,GPIO_Label
PA4.GPIO_Label=SPI1_NSS
PA4.Locked=true
PA4.PinState=GPIO_PIN_SET
PA4.Signal=GPIO_Output
PA5.GPIOParameters=GPIO_Speed
PA5.GPIO_Speed=GPIO_SPEED_FREQ_HIGH
PA5.Mode=Full_Duplex_Master
PA5.Signal=SPI1_SCK
PA6.GPIOParameters=GPIO_Speed
PA6.GPIO_Speed=GPIO_SPEED_FREQ_HIGH
PA6.Mode=Full_Duplex_Master
PA6.Signal=SPI1_MISO
PA7.Mode=RMII
PA7.Signal=ETH_CRS_DV
PA8.Mode=I2C
PA8.Signal=I2C3_SCL
PB10.GPIOParameters=GPIO_Speed,PinState,GPIO_Label
PB10.GPIO_Label=CXN_REL2
PB10.GPIO_Speed=GPIO_SPEED_FREQ_MEDIUM
PB10.Locked=true
PB10.PinState=GPIO_PIN_RESET
PB10.Signal=GPIO_Output
PB11.GPIOParameters=GPIO_Speed,PinState,GPIO_Label
PB11.GPIO_Label=CXN_REL1
PB11.GPIO_Speed=GPIO_SPEED_FREQ_MEDIUM
PB11.Locked=true
PB11.PinState=GPIO_PIN_RESET
PB11.Signal=GPIO_Output
PB12.GPIOParameters=PinState,GPIO_Label
PB12.GPIO_Label=SPI2_NSS
PB12.Locked=true
PB12.PinState=GPIO_PIN_SET
PB12.Signal=GPIO_Output
PB13.Locked=true
PB13.Mode=Full_Duplex_Master
PB13.Signal=SPI2_SCK
PB14.Locked=true
PB14.Mode=Full_Duplex_Master
PB14.Signal=SPI2_MISO
PB15.Locked=true
PB15.Mode=Full_Duplex_Master
PB15.Signal=SPI2_MOSI
PB2.GPIOParameters=PinState,GPIO_Label
PB2.GPIO_Label=LED_BLUE
PB2.Locked=true
PB2.PinState=GPIO_PIN_SET
PB2.Signal=GPIO_Output
PB5.GPIOParameters=GPIO_Speed
PB5.GPIO_Speed=GPIO_SPEED_FREQ_HIGH
PB5.Mode=Full_Duplex_Master
PB5.Signal=SPI1_MOSI
PC1.Mode=RMII
PC1.Signal=ETH_MDC
PC10.GPIOParameters=GPIO_Speed,GPIO_PuPd
PC10.GPIO_PuPd=GPIO_PULLUP
PC10.GPIO_Speed=GPIO_SPEED_FREQ_HIGH
PC10.Mode=Full_Duplex_Master
PC10.Signal=SPI3_SCK
PC11.GPIOParameters=GPIO_Speed
PC11.GPIO_Speed=GPIO_SPEED_FREQ_HIGH
PC11.Mode=Full_Duplex_Master
PC11.Signal=SPI3_MISO
PC12.GPIOParameters=GPIO_Speed
PC12.GPIO_Speed=GPIO_SPEED_FREQ_HIGH
PC12.Locked=true
PC12.Mode=Full_Duplex_Master
PC12.Signal=SPI3_MOSI
PC13.GPIOParameters=PinState,GPIO_Label
PC13.GPIO_Label=FGEN_nDIV10
PC13.Locked=true
PC13.PinState=GPIO_PIN_SET
PC13.Signal=GPIO_Output
PC14/OSC32_IN.GPIOParameters=PinState,GPIO_Label
PC14/OSC32_IN.GPIO_Label=FGEN_DIV8
PC14/OSC32_IN.Locked=true
PC14/OSC32_IN.PinState=GPIO_PIN_SET
PC14/OSC32_IN.Signal=GPIO_Output
PC15/OSC32_OUT.GPIOParameters=PinState,GPIO_Label
PC15/OSC32_OUT.GPIO_Label=FGEN_DIV4
PC15/OSC32_OUT.Locked=true
PC15/OSC32_OUT.PinState=GPIO_PIN_SET
PC15/OSC32_OUT.Signal=GPIO_Output
PC4.Mode=RMII
PC4.Signal=ETH_RXD0
PC5.Mode=RMII
PC5.Signal=ETH_RXD1
PC9.Mode=I2C
PC9.Signal=I2C3_SDA
PD0.GPIOParameters=GPIO_Label
PD0.GPIO_Label=ADC1_RVS1
PD0.Locked=true
PD0.Signal=GPIO_Input
PD1.GPIOParameters=GPIO_Label
PD1.GPIO_Label=ADC1_RVS2
PD1.Locked=true
PD1.Signal=GPIO_Input
PD10.GPIOParameters=GPIO_Label
PD10.GPIO_Label=MCU_nISNK
PD10.Locked=true
PD10.Signal=GPXTI10
PD11.GPIOParameters=GPIO_Label
PD11.GPIO_Label=MCU_nISRC
PD11.Locked=true
PD11.Signal=GPXTI11
PD12.Locked=true
PD12.Mode=I2C
PD12.Signal=I2C4_SCL
PD13.Locked=true
PD13.Mode=I2C
PD13.Signal=I2C4_SDA
PD14.GPIOParameters=GPIO_Label
PD14.GPIO_Label=SR_OUT
PD14.Locked=true
PD14.Signal=GPIO_Input
PD15.GPIOParameters=GPIO_Label
PD15.GPIO_Label=SR_LAT
PD15.Locked=true
PD15.Signal=GPIO_Output
PD9.GPIOParameters=GPIO_Label
PD9.GPIO_Label=MCU_nTDS
PD9.Locked=true
PD9.Signal=GPXTI9
PE10.GPIOParameters=GPIO_Label
PE10.GPIO_Label=MCU_DEFAULT
PE10.Locked=true
PE10.Signal=GPIO_Input
PE12.GPIOParameters=GPIO_Speed,GPIO_Label
PE12.GPIO_Label=CXN_REL6
PE12.GPIO_Speed=GPIO_SPEED_FREQ_MEDIUM
PE12.Locked=true
PE12.Signal=GPIO_Output
PE13.GPIOParameters=GPIO_Speed,GPIO_Label
PE13.GPIO_Label=CXN_REL5
PE13.GPIO_Speed=GPIO_SPEED_FREQ_MEDIUM
PE13.Locked=true
PE13.Signal=GPIO_Output
PE14.GPIOParameters=GPIO_Speed,GPIO_Label
PE14.GPIO_Label=CXN_REL4
PE14.GPIO_Speed=GPIO_SPEED_FREQ_MEDIUM
PE14.Locked=true
PE14.Signal=GPIO_Output
PE15.GPIOParameters=GPIO_Speed,GPIO_Label
PE15.GPIO_Label=CXN_REL3
PE15.GPIO_Speed=GPIO_SPEED_FREQ_MEDIUM
PE15.Locked=true
PE15.Signal=GPIO_Output
PE2.Mode=RX_Only_Simplex_Unidirect_Master
PE2.Signal=SPI4_SCK
PE4.GPIOParameters=PinState,GPIO_Label
PE4.GPIO_Label=SPI4_NSS
PE4.Locked=true
PE4.PinState=GPIO_PIN_RESET
PE4.Signal=GPIO_Output
PE5.Mode=RX_Only_Simplex_Unidirect_Master
PE5.Signal=SPI4_MISO
PE7.GPIOParameters=GPIO_Label
PE7.GPIO_Label=TRIG_IN
PE7.Locked=true
PE7.Signal=GPXTI7
PE8.GPIOParameters=GPIO_Label
PE8.GPIO_Label=TRIG_OUT
PE8.Locked=true
PE8.Signal=GPIO_Output
PE9.GPIOParameters=GPIO_Label
PE9.GPIO_Label=TRIG_EN
PE9.Locked=true
PE9.Signal=GPIO_Output
PF0.GPIOParameters=PinState,GPIO_Label
PF0.GPIO_Label=FGEN_DIV2
PF0.Locked=true
PF0.PinState=GPIO_PIN_SET
PF0.Signal=GPIO_Output
PF11.GPIOParameters=PinState,GPIO_Label
PF11.GPIO_Label=LED_RED
PF11.Locked=true
PF11.PinState=GPIO_PIN_SET
PF11.Signal=GPIO_Output
PF12.GPIOParameters=PinState,GPIO_Label
PF12.GPIO_Label=LED_GREEN
PF12.Locked=true
PF12.PinState=GPIO_PIN_SET
PF12.Signal=GPIO_Output
PF6.GPIOParameters=GPIO_Speed,PinState,GPIO_Label
PF6.GPIO_Label=SPI5_NSS
PF6.GPIO_Speed=GPIO_SPEED_FREQ_HIGH
PF6.Locked=true
PF6.PinState=GPIO_PIN_SET
PF6.Signal=GPIO_Output
PF7.Mode=Full_Duplex_Master
PF7.Signal=SPI5_SCK
PF8.Mode=Full_Duplex_Master
PF8.Signal=SPI5_MISO
PF9.Mode=Full_Duplex_Master
PF9.Signal=SPI5_MOSI
PG11.Locked=true
PG11.Mode=RMII
PG11.Signal=ETH_TX_EN
PG12.GPIOParameters=GPIO_Speed,PinState,GPIO_Label
PG12.GPIO_Label=DAC2_nLDAC
PG12.GPIO_Speed=GPIO_SPEED_FREQ_HIGH
PG12.Locked=true
PG12.PinState=GPIO_PIN_SET
PG12.Signal=GPIO_Output
PG13.Locked=true
PG13.Mode=RMII
PG13.Signal=ETH_TXD0
PG14.Locked=true
PG14.Mode=RMII
PG14.Signal=ETH_TXD1
PG2.GPIOParameters=GPIO_Label
PG2.GPIO_Label=SR_CLK
PG2.Locked=true
PG2.Signal=GPIO_Output
PG3.GPIOParameters=GPIO_Label
PG3.GPIO_Label=SR_DAT
PG3.Locked=true
PG3.Signal=GPIO_Output
PG4.GPIOParameters=PinState,GPIO_Label
PG4.GPIO_Label=EEPROM_WP
PG4.Locked=true
PG4.PinState=GPIO_PIN_SET
PG4.Signal=GPIO_Output
PG5.GPIOParameters=GPIO_Label
PG5.GPIO_Label=MCU_CURR_SENS_1kR
PG5.Locked=true
PG5.Signal=GPIO_Output
PG6.GPIOParameters=PinState,GPIO_Label
PG6.GPIO_Label=MCU_CURR_SENS_100R
PG6.Locked=true
PG6.PinState=GPIO_PIN_RESET
PG6.Signal=GPIO_Output
PG7.GPIOParameters=PinState,GPIO_Label
PG7.GPIO_Label=MCU_CURR_SENS_10R
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

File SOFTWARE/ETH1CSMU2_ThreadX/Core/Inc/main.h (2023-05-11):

/* USER CODE BEGIN Header */
/**
  ******************************************************************************
  * @file           : main.h
  * @brief          : Header for main.c file.
  *                   This file contains the common defines of the application.
  ******************************************************************************
  * @attention
  *
  * Copyright (c) 2023 STMicroelectronics.
  * All rights reserved.
  *
  * This software is licensed under terms that can be found in the LICENSE file
  * in the root directory of this software component.
  * If no LICENSE file comes with this software, it is provided AS-IS.
  *
  ******************************************************************************
  */
/* USER CODE END Header */

/* Define to prevent recursive inclusion -------------------------------------*/
#ifndef __MAIN_H
#define __MAIN_H

#ifdef __cplusplus
extern "C" {
#endif

/* Includes ------------------------------------------------------------------*/
#include "stm32f7xx_hal.h"
#include "stm32f7xx_ll_system.h"
#include "stm32f7xx_ll_gpio.h"
#include "stm32f7xx_ll_exti.h"
#include "stm32f7xx_ll_bus.h"
#include "stm32f7xx_ll_cortex.h"
#include "stm32f7xx_ll_rcc.h"
#include "stm32f7xx_ll_utils.h"
#include "stm32f7xx_ll_pwr.h"
#include "stm32f7xx_ll_dma.h"

/* Private includes ----------------------------------------------------------*/
/* USER CODE BEGIN Includes */

/* USER CODE END Includes */

/* Exported types ------------------------------------------------------------*/
/* USER CODE BEGIN ET */

/* USER CODE END ET */

/* Exported constants --------------------------------------------------------*/
/* USER CODE BEGIN EC */

/* USER CODE END EC */

/* Exported macro ------------------------------------------------------------*/
/* USER CODE BEGIN EM */

/* USER CODE END EM */

/* Exported functions prototypes ---------------------------------------------*/
void Error_Handler(void);

/* USER CODE BEGIN EFP */

/* USER CODE END EFP */
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

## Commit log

2022-08-07 Hardware design
    [Connect.kicad_sch, Control.kicad_sch, ETH1CSMU2.kicad_pcb, ETH1CSMU2.kicad_sch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]
2022-08-09 Hardware design.
    [Connect.kicad_sch, Control.kicad_sch, ETH1CSMU2.csv, ETH1CSMU2.kicad_sch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]
2022-08-11 Hardware and software development
    [Connect.kicad_sch, Control.kicad_sch, ETH1CSMU2.kicad_sch, Ethernet.kicad_sch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]
2022-08-11 CRC check
    [Connect.kicad_sch, ETH1CSMU2.kicad_sch, Ethernet.kicad_sch, MCU.kicad_sch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]
2022-08-14 PCB layout
    [ETH1CSMU2.csv, ETH1CSMU2.kicad_pcb, ETH1CSMU2.kicad_sch, ETH1CSMU2.ods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]
2022-08-15 Changes in schematic.
    [Connect.kicad_sch, Control.kicad_sch, ETH1CSMU2.kicad_sch, Ethernet.kicad_sch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]
2022-08-26 Bug fixes.
    [Connect.kicad_sch, Control.kicad_sch, ETH1CSMU2.kicad_sch, Ethernet.kicad_sch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]
2022-08-26 Schematic modification and GPIO setup.
    [ETH1CSMU2.kicad_sch, Source.kicad_sch]
2022-08-29 Added two 10uF capacitors in Frontend page.
    [ETH1CSMU2.kicad_sch, Frontend.kicad_sch]
2023-01-22 Software development
    [Connect.kicad_sch, Control.kicad_sch, ETH1CSMU2.kicad_sch, Ethernet.kicad_sch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]
2023-03-04 Converter HW to KiCAD 7.0. Fixed 3D model paths.
    [Connect.kicad_sch, Control.kicad_sch, ETH1CSMU2.kicad_sch, Ethernet.kicad_sch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]
2023-03-26 Software development and hardware changes.
    [Source.kicad_sch]
2023-03-27 Software development, added comments to schematic.
    [Frontend.kicad_sch, Source.kicad_sch]
2023-04-01 Software development and hardware changes. FGEN code works.
    [Control.kicad_sch, ETH1CSMU2.kicad_sch, MCU.kicad_sch, Source.kicad_sch]
2023-04-18 AD7980 test works.
    [Control.kicad_sch, Measure.kicad_sch]
2023-05-07 ThreadX software development.
2023-05-10 ThreadX TCP server works.
2023-05-19 Calibration software development. Problems with positive voltage. Need to add gain calibration.
2023-05-20 DC calibration works. AC signal function works.
2023-07-12 Hardware fix. Created README file
    [Connect.kicad_sch, Control.kicad_sch, ETH1CSMU2.kicad_sch, Ethernet.kicad_sch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]
